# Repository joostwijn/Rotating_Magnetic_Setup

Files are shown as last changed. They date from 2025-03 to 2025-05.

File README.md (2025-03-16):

# Magnetic_Rotating_Setup
This repository documents a rotating magnet setup that uses a stepper motor to precisely control two parallel rotating magnets. The system is designed for applications requiring controlled magnetic torque while minimizing unwanted field gradients.

**Repository Structure**  
The project is divided into three main chapters:

**1. Parts & Assembly** – Component list, STP and SLDASM files of the entire assembly, SLDPRT files of all parts, DXF files for lasercutting, STL files for 3D printing.  
**2. Electronics** – Introduction to the electronic componets used, wiring diagram, Arduino code, Nextion code.  
**3. Magnets** – Field-shaping algorithm.

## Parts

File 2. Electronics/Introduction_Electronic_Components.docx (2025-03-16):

This file contains a brief explanation of the different electronic components used in the Rotating Magnetic Setup. These components include the 12V/5A power supply, Arduino UNO R3, Nema 17 stepper motor, DRV8825 stepper driver, and Nextion display 2.4 inch (NX3224T024). The wiring of these components can be found in the file ”Wire_Diagram”.

12V/5A power supply
The system is powered by a 12V/5A power supply, which in turn is connected to a 230V mains socket. For safety and convenience, the 230V supply first passes through a three-pin fused switch connector before reaching the power supply.
To protect the electronics from damaging voltage spikes, a 100μF (rated at 50V) capacitor is placed across the 12V power supply’s positive and negative terminals, mitigating any surge that might otherwise harm the components.
The 12V output is distributed in two ways: it directly powers the stepper motor and supplies the Arduino UNO R3.

Arduino UNO R3
The Arduino UNO R3 is used to communicate with the Nextion display and uses the Nextion’s input to drive the stepper motor. The Arduino is programmed using C++ in the dedicated Arduino IDE (https://www.arduino.cc/en/software). The Arduino features an onboard step-down converter that supports up to 12V, allowing it to operate safely while maintaining the ability to upload code via USB. When a USB cable is connected, the Arduino automatically switches to USB power. The Arduino’s regulated 5V output is used to power both the Nextion display and the stepper driver.

NEMA 17 stepper motor
The NEMA 17 stepper motor is powered directly by the 12V power supply and controlled through a stepper driver. The Arduino UNO sends pulse signals to the stepper driver based on input from the Nextion display, determining the motor's speed and direction. The NEMA 17 can deliver a torque of up to 5.0 kg·cm (0.49 N·m). If higher torque is required, a NEMA 23 stepper motor can be used, but this requires a different stepper driver.

The NEMA 17 generates significant noise and vibrations at low rotation speeds. These can be reduced by enabling microstepping (smaller steps result in fewer vibrations), lowering the current limit on the stepper driver (see next paragraph), and including rubber O-rings in the stepper motor mounting.

DRV8825 stepper driver
The DRV8825 stepper motor driver receives pulse signals from the Arduino UNO to control the NEMA 17 stepper motor. It supports microstepping up to 1/32 steps and operates at 8.2V to 45V, supplying up to 2.5A per coil with sufficient cooling. The current limit must be manually set using the build-in potentiometer to match the motor's rated current (see https://www.makerguides.com/drv8825-stepper-motor-driver-arduino-tutorial/ for instructions). A heatsink or active cooling is required at high currents (<1 A) to prevent overheating.

Nextion display 2.4 inch (NX3224T024)
The Nextion 2.4-inch (NX3224T024) display is a resistive touchscreen that operates independently from the Arduino. It communicates with the Arduino via a hexadecimal protocol, sending commands for speed, direction, and the number of turns the stepper motor should complete.

Using a separate UI module reduces processing load on the Arduino and enables independent display operation. The Nextion is programmed using the Nextion Editor, which provides a graphical interface for designing screens and handling interactions (https://nextion.tech/editor_guide/).

Code uploads require an ADLivery CP2102 USB-to-serial adapter, along with its corresponding driver (https://www.silabs.com/developer-tools/usb-to-uart-bridge-vcp-drivers?tab=downloads). Proper installation of the driver is necessary for successful communication between the computer and the display.

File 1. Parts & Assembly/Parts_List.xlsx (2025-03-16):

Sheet: Structural_Components
Component | Quantity | Notes
20x20x500 aluminum profile | 2
20x40x160 aluminum profile | 5
Angle backets 20x20 | 12
Nema-17 angle bracket | 1
O-ring 28x3.1 | 4 | Supports for the setup to reduce vibrations and noise
O-ring 6x1.9 | 4 | Used as washers for the mounting screws of the stepper motor to reduce vibrations and noise
Washer M5 | 31
T-nut M5 | 31
Nut M3 | 9
Hex. socket screw M5x12 | 31
Hex. socket screw M3x6 | 17
Hex. socket screw M3x8 | 2
Hex. socket screw M3x20 | 1
Hex. Bolt M3x8 | 4
Threaded inserts M3x4x5 | 8

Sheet: Manufactured_Parts
Component | Quantity | Manufacturing technique | Material
Electronics mounting plate | 1 | 3D printing (FDM) | PLA
Magnetic mount support | 2 | 3D printing (FDM) | PLA
Magnetic slots | 2 | 3D printing (FDM) | PLA
Axis | 1 | 3D printing (FDM) | PLA
Actuation medium holder | 1 | 3D printing (FDM) | PLA
Back plate electronic casing | 1 | Laser cutting | PMMA (t = 3mm)
Frontplate electronic casing | 1 | Laser cutting | PMMA (t = 3mm)
Left side plate electronic casing | 1 | Laser cutting | PMMA (t = 3mm)
Right side plate electronic casing | 1 | Laser cutting | PMMA (t = 3mm)
Back top plate electronic casing | 1 | Laser cutting | PMMA (t = 3mm)
Front top plate electronic casing | 1 | Laser cutting | PMMA (t = 3mm)

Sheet: Electronics
Component | Quantity | Notes
Nema 17 stepper motor | 1
DRV8825 stepper driver | 1
Arduino UNO R3 | 1
Arduino UNO R3 base | 1 | Included in Arduino UNO R3 package
Power Supply 12V/5A | 1
3-pin connector with switch and fuse | 1 | Fuse is included in package
Breadboard 1/2 size | 1
Nextion display 2.4 inch (NX3224T024) | 1
Dupont wires 20 mm | 24
Capacitor 100 μF | 1

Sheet: Magnets
Component | Quantity | Notes
NdFeB Magnets 3x3 mm | 20

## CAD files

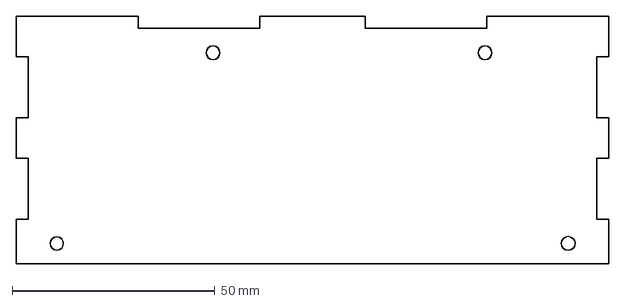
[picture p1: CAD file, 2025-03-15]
1. Parts & Assembly/DXF/PMMA_3mm_1x_BackP.DXF
146.0 x 61.0 mm

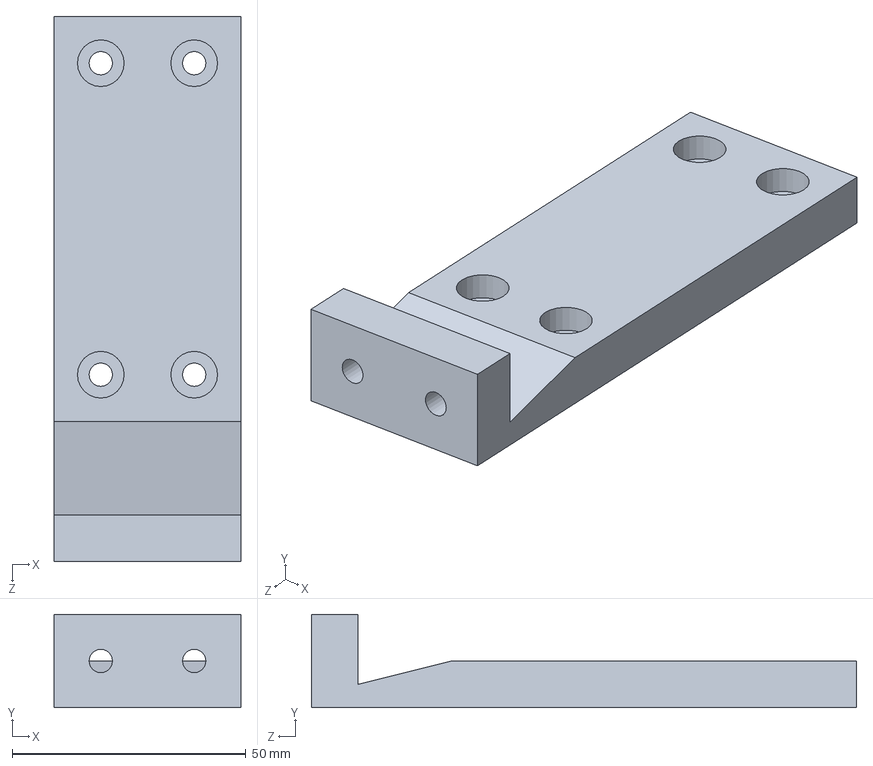
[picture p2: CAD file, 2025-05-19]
1. Parts & Assembly/SLDPRT/Tube_Setter.SLDPRT
40.0 x 20.0 x 116.7 mm

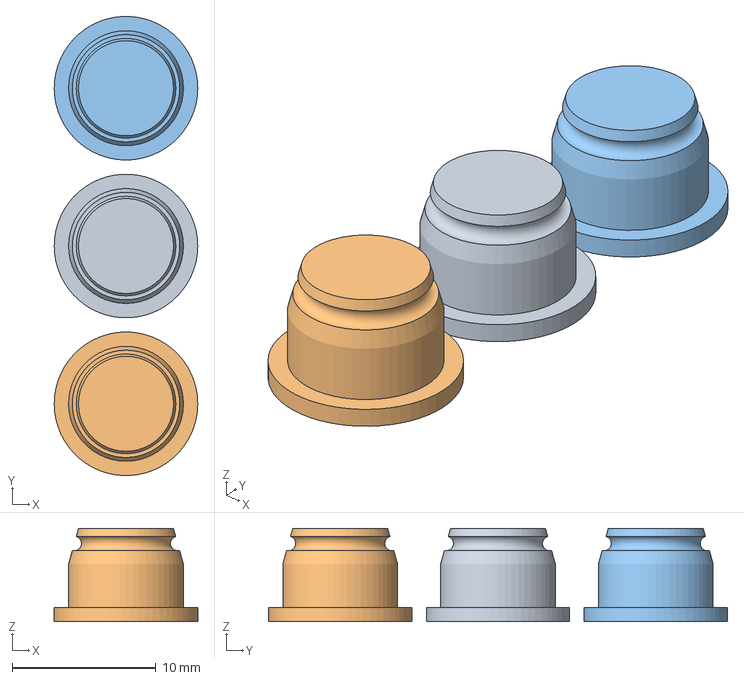
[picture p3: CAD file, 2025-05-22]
1. Parts & Assembly/STL/2x_TubeCap.3mf
10.0 x 32.0 x 6.50 mm
2x_TubeCap.STL x 3

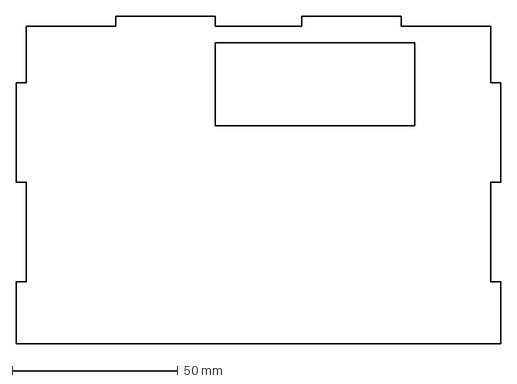
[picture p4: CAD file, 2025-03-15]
1. Parts & Assembly/DXF/PMMA_3mm_1x_TopPB.DXF
146.0 x 98.7 mm

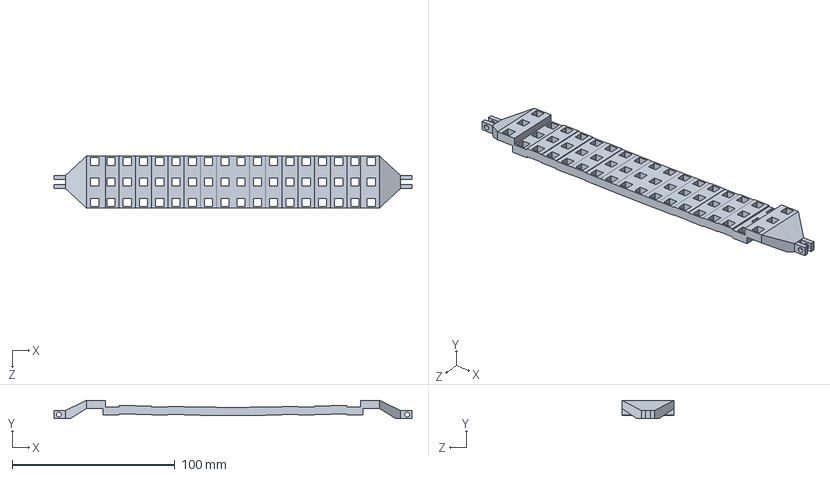
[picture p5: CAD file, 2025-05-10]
1. Parts & Assembly/SLDPRT/Slots.SLDPRT
220.0 x 11.3 x 32.0 mm

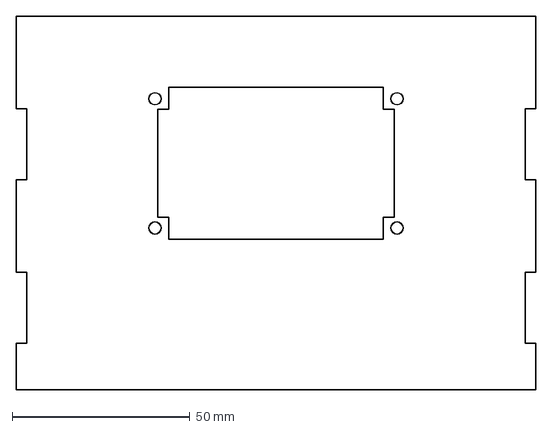
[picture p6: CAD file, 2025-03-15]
1. Parts & Assembly/DXF/PMMA_3mm_1x_TopPF.DXF
146.0 x 105.0 mm

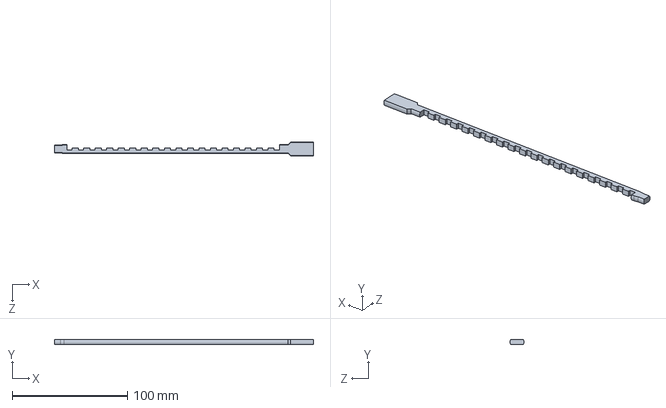
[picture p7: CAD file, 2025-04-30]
1. Parts & Assembly/SLDPRT/Measure_Guide.SLDPRT
225.0 x 4.00 x 11.9 mm

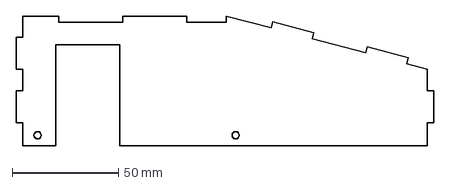
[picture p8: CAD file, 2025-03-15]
1. Parts & Assembly/DXF/PMMA_3mm_1x_LeftSP.DXF
196.0 x 61.0 mm

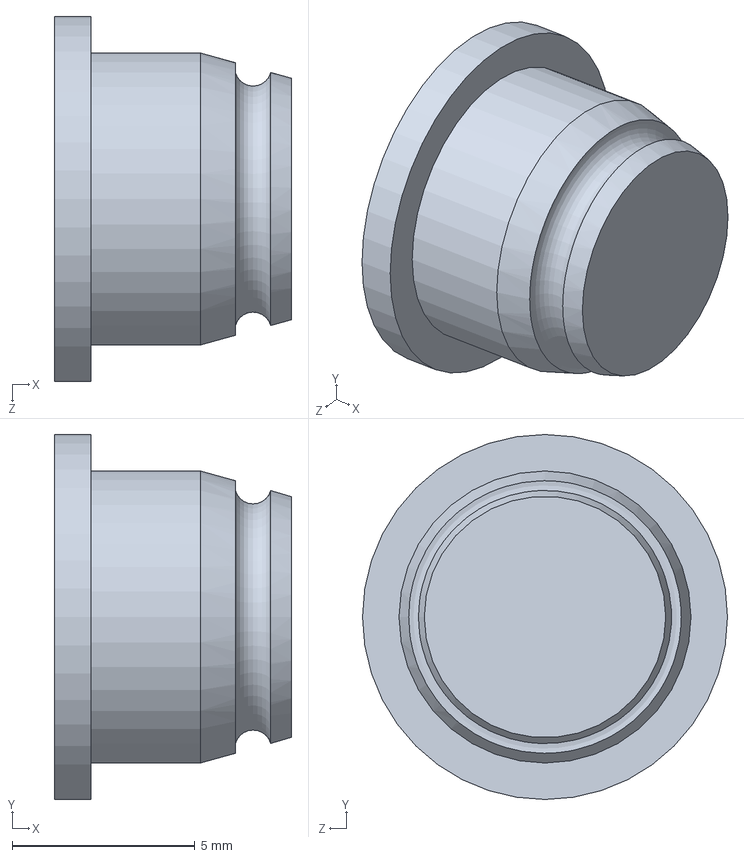
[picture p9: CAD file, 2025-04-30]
1. Parts & Assembly/SLDPRT/Tube_Cap.SLDPRT
6.50 x 10.0 x 10.0 mm

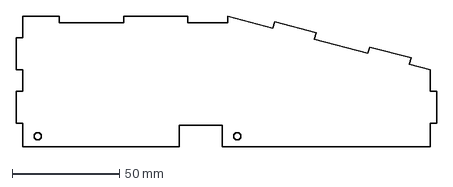
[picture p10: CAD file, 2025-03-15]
1. Parts & Assembly/DXF/PMMA_3mm_1x_RightSP.DXF
196.0 x 61.0 mm

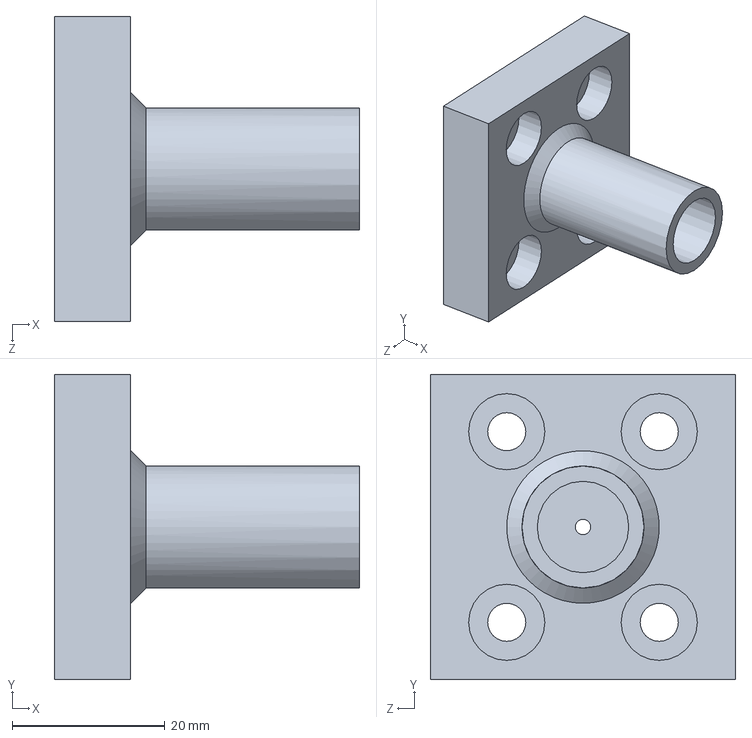
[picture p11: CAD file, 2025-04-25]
1. Parts & Assembly/SLDPRT/Axis.SLDPRT
40.0 x 40.0 x 40.0 mm

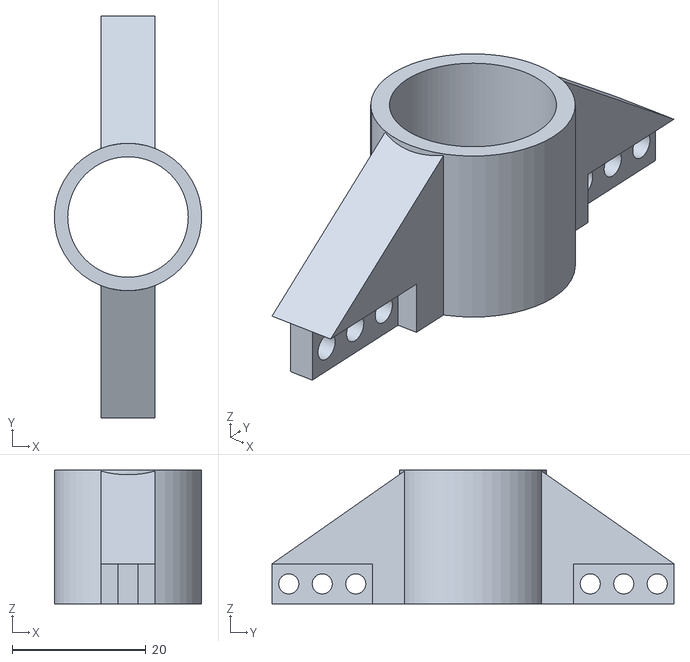
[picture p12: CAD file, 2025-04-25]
1. Parts & Assembly/STL/1x_MR.STL
22.0 x 60.0 x 20.0

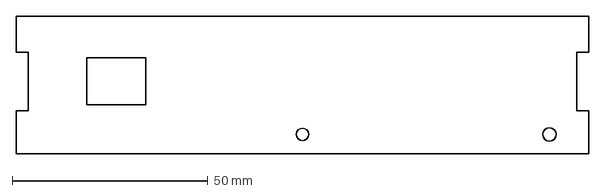
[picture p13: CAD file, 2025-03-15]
1. Parts & Assembly/DXF/PMMA_3mm_1x_FrontP.DXF
146.0 x 35.2 mm

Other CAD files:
1. Parts & Assembly/STL/1x_Tube_Setter.3mf
1. Parts & Assembly/STL/2x_Slots.STL
1. Parts & Assembly/STL/1x_MG.STL
1. Parts & Assembly/SLDPRT/Mount_Right.SLDPRT
1. Parts & Assembly/STL/1x_Axis.STL
1. Parts & Assembly/SLDPRT/2020_Single_ALPROFILE_500mm.SLDPRT
1. Parts & Assembly/SLDPRT/2040_Double_ALPROFILE_160mm.SLDPRT
1. Parts & Assembly/SLDPRT/Arduino_UNO_Rev3_Base.SLDPRT
1. Parts & Assembly/SLDPRT/BackPlate.SLDPRT
1. Parts & Assembly/SLDPRT/Bracket-90deg.SLDPRT
1. Parts & Assembly/SLDPRT/Bracket_90deg.SLDPRT
1. Parts & Assembly/SLDPRT/Breadboard.SLDPRT
1. Parts & Assembly/SLDPRT/Connector_Switch_And_Fuse.SLDPRT
1. Parts & Assembly/SLDPRT/Electronic_Bottom_Plate.SLDPRT
1. Parts & Assembly/SLDPRT/FrontPlate.SLDPRT
1. Parts & Assembly/SLDPRT/Left_Sideplate.SLDPRT
1. Parts & Assembly/SLDPRT/M2X3_Insert.SLDPRT
1. Parts & Assembly/SLDPRT/M3X4_Insert.SLDPRT
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

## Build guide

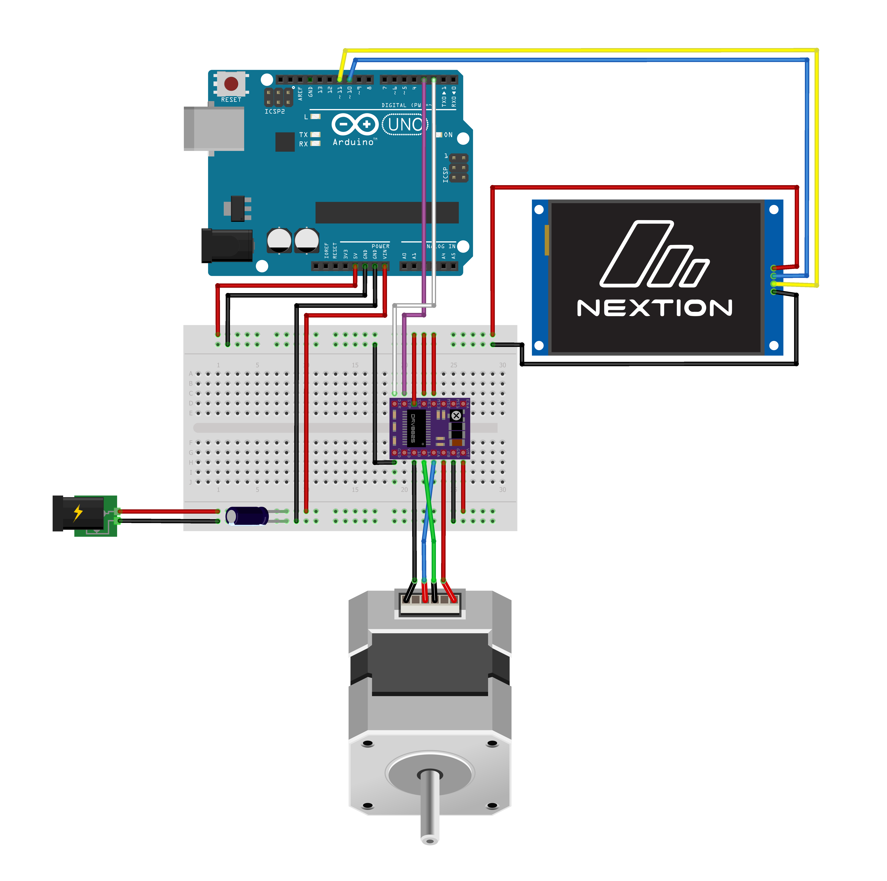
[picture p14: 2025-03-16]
2. Electronics/Wiring_Diagram_bb.png

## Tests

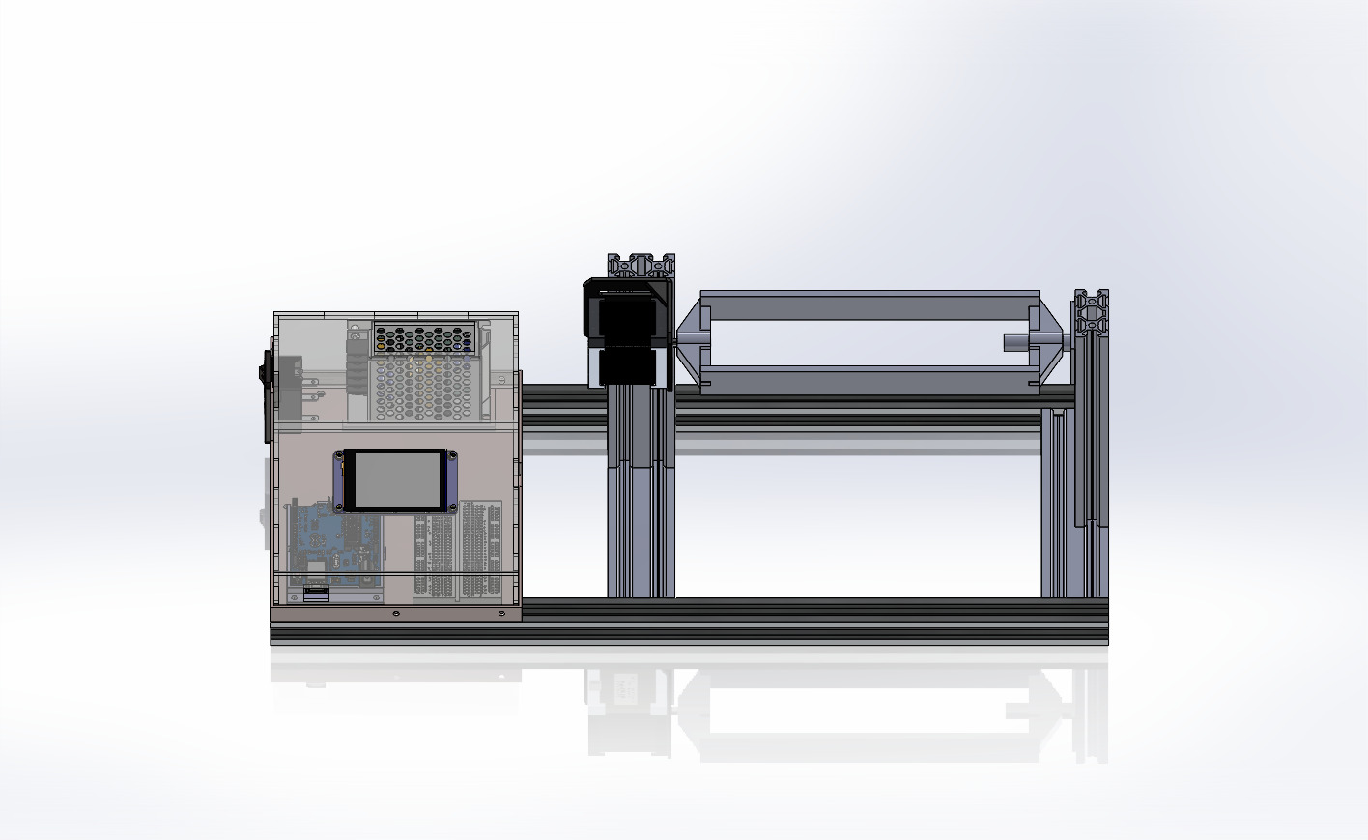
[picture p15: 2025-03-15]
1. Parts & Assembly/JPG/New_Test_Setup.JPG

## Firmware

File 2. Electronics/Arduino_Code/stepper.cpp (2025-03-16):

#include <Arduino.h>
#include "stepper.h"

// --- Setting up the stepper motor and driver ---
// Create an AccelStepper object in DRIVER mode so that the Accel library knows we are using a driver (DRV8825).
// STEP_PIN: A pulse signal is sent to this pin. Each pulse moves the motor by one step (or microstep, depending on the driver settings).
// DIR_PIN: This pin controls the rotation direction. HIGH typically means clockwise (CW), and LOW means counterclockwise (CCW).
// STEP_PIN and DIR_PIN are defined in stepper.h.
AccelStepper stepper(AccelStepper::DRIVER, STEP_PIN, DIR_PIN);

// --- Constants for step calculation ---
// Number of full steps per revolution (Nema 17 = 200 steps per rev)
const int FULL_STEPS_PER_REV = 200;   
// Microstepping multiplier: For 1/16 microstepping, a multiplier of 16 is needed in order to calculate the number of steps per rotation. Change accordingly.
const int MICROSTEP_MULTIPLIER = 16;    
// Total steps per revolution in microstepping mode
const int STEPS_PER_REV = FULL_STEPS_PER_REV * MICROSTEP_MULTIPLIER;  

// Flag indicating if the motor should run continuously
bool Continuous_Mode = false;

// ---------------------------------------------------------------------
// Initializes the stepper motor and sets up serial communication.
void initStepper() {
  Serial.begin(9600);
  stepper.setMaxSpeed(16000); // Set the maximum speed in steps/second. 
  // Set the current limit higher if the stepper cannot achieve the max speed https://www.makerguides.com/drv8825-stepper-motor-driver-arduino-tutorial/.
}

// ---------------------------------------------------------------------
// Updates the motor parameters.
// Parameters:
//   newSpeed: Desired speed in rotations per second (RPS).
//   newTurns: Number of full revolutions to move (0 for continuous motion).
//   newDir: 'R' for clockwise, 'L' for counterclockwise. Any other value stops the motor.
void updateStepper(float newSpeed, int newTurns, char newDir) {
  // Determine the direction factor: 1 for clockwise, -1 for counterclockwise.
  int directionFactor = (newDir == 'R') ? 1 : (newDir == 'L') ? -1 : 0;

  // Stop the motor if an invalid direction is provided, otherwise calculate the speed.
  if (directionFactor == 0) {
    Continuous_Mode = false;
    stepper.stop(); // Stop immediately.
    stepper.moveTo(stepper.currentPosition());  // Force the target to be the current position to eliminate any residual motion.
  } else {
    int speedStepsPerSec = newSpeed * STEPS_PER_REV;  // Convert the speed from rotations per second (RPS) to steps per second.

    // Do continuous turning if the number of turns is set to zero, otherwise move a specified number of revolutions.
    if (newTurns == 0) {
      // Continuous motion mode: run indefinitely at the specified speed.
      Continuous_Mode = true;
      stepper.setSpeed(directionFactor * speedStepsPerSec);
    } else {
      // Fixed-turn mode: move a specified number of revolutions.
      Continuous_Mode = false;
      long targetPosition = stepper.currentPosition() + (long)directionFactor * newTurns * STEPS_PER_REV;  // Calculate the target position relative to the current position.
      stepper.moveTo(targetPosition); // Set the target position.
      stepper.setSpeed(directionFactor * speedStepsPerSec); // Set the motor speed AFTER setting the target position.
    }
  }
}

// ---------------------------------------------------------------------
// Runs the motor based on the current mode.
// This function is called in the .ino file.
void runStepper() {
  if (Continuous_Mode) {
    stepper.runSpeed();         // Run continuously at a constant speed.
  } else {
    stepper.runSpeedToPosition(); // Move toward the target position at constant speed.
  }
}

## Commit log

2025-03-15 Uploading documents
    [1x_AxisJFW.STL, 1x_EBPJFW.STL, 2040_Double_ALPROFILE_160mm.SLDPRT, ALUMINIUM_PROFILE_20m x 20mm x 500mm.SLDPRT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]
2025-03-15 Ignoring files with dolars
    [1x_AxisJFW.STL, 1x_EBPJFW.STL, 2040_Double_ALPROFILE_160mm.SLDPRT, ALUMINIUM_PROFILE_20m x 20mm x 500mm.SLDPRT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]
2025-03-15 More doccuments but dolar signs are needed
    [1x_AxisJFW.STL, 1x_EBPJFW.STL, 2040_Double_ALPROFILE_160mm.SLDPRT, ALUMINIUM_PROFILE_20m x 20mm x 500mm.SLDPRT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]
2025-03-15 Better folders
    [1x_AxisJFW.STL, 1x_EBPJFW.STL, 2020_Single_ALPROFILE_500mm.SLDPRT, 2040_Double_ALPROFILE_160mm.SLDPRT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]
2025-03-15 .gitignore works finally
    [Parts_List.xlsx]
2025-03-16 added electronics section
    [Parts_List.xlsx]
2025-04-09 Checked 0.1 mm
2025-04-17 Changes in SW and saving before to main
    [1x_AxisJFW.STL, Axis.SLDPRT, Plain_Bushing_16x18x20.SLDPRT, Plain_Bushing_5x7x5.SLDPRT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]
2025-04-23 A lot in solidworks
    [1x_MLJFW.STL, 1x_MRJFW.STL, M2X3_Insert.SLDPRT, Mount_Left.SLDPRT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]
2025-04-30 Voor download
    [1x_MG.STL, 2x_TubeCap.STL, Measure_Guide.SLDPRT, Slots.SLDPRT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]
2025-05-02 New slots
    [2x_Slots.STL]
2025-05-10 Save to be sure
    [2x_Slots.3mf, 2x_Slots.STL, Slots.SLDPRT]
2025-05-19 New Save
    [1x_Tube_Setter.STL, Tube_Setter.SLDPRT]
2025-07-01 Magnetic Susceptibility Added
    [2x_Slots.3mf]
